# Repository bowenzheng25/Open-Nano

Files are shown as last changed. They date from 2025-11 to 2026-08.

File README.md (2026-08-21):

# Open Nano

This repository describes how to build and use your own nanopositioner. 

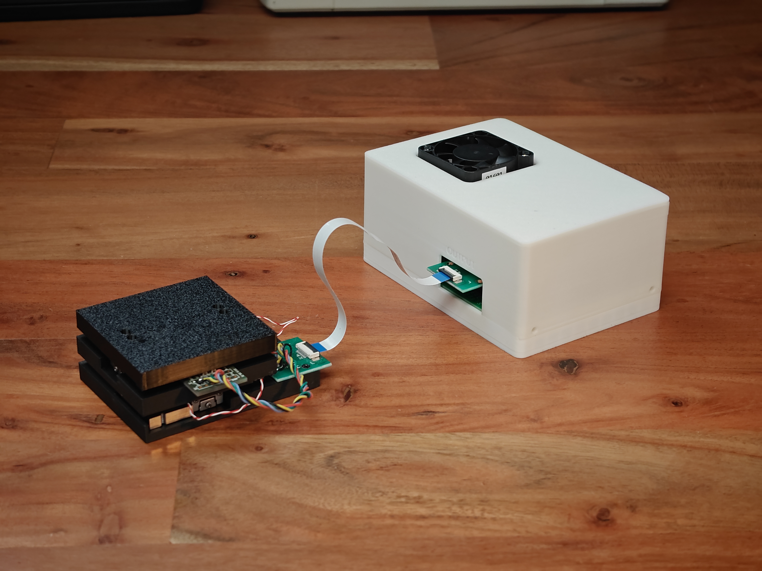
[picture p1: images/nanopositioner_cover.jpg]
nanopositioner assembly


## Getting Started

1.  Go over this readme file for high-level overview
2.  Obtain the parts listed in the [Bill of Materials](https://github.com/bwnzhng/Open-Nano/blob/main/assembly/bom.md)
3.  Assemble the instrument and electronics
4.  Configure the hardware to fit your needs
5.  Upload firmware using VSCode with PlattformIO plugin
6.  Calibrate axis

## Design Files

Files (ie .stl and .dxf) for your reproduction are saved in [the assembly folder](https://github.com/bwnzhng/Open-Nano/tree/main/assembly/cad)

The CAD files are produced in Fusion360. You can get free access through the educational license. 

Otherwise, engineering drawings are attached for you to reproduce the part in your choice of CAD software as the designs are relatively straightforward.

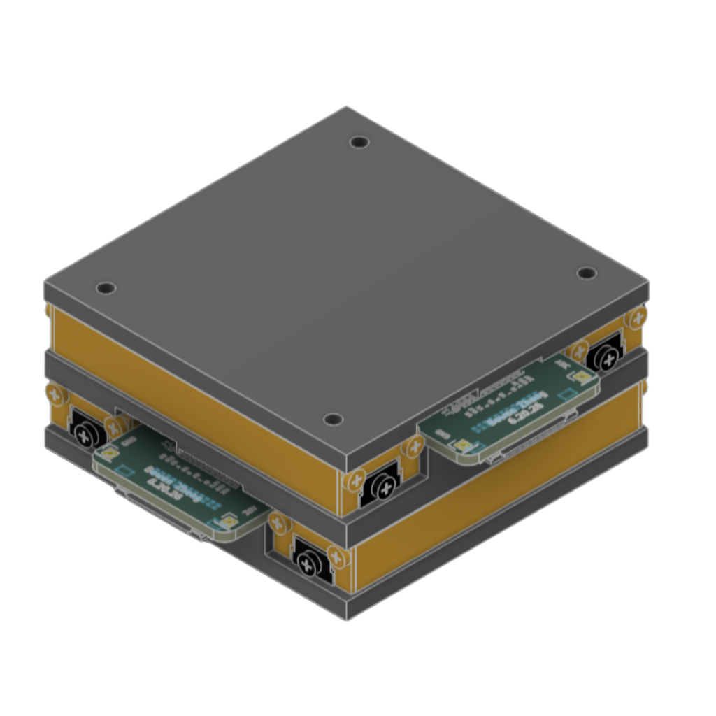
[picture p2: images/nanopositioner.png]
Nanopositioner

## Electronics

The PCB schematics are designed in KICAD. No SMD soldering is required since through hole electronic components are used for easier hands-on assembly.

Please note you will need to attach heatsinks to the amplifiers to maintain optimal performance.

This repository also contains fabrication files that can directly uploaded to a PCB manufacturer (located in [the electronics folder](https://github.com/bwnzhng/Open-Nano/tree/main/electronics))

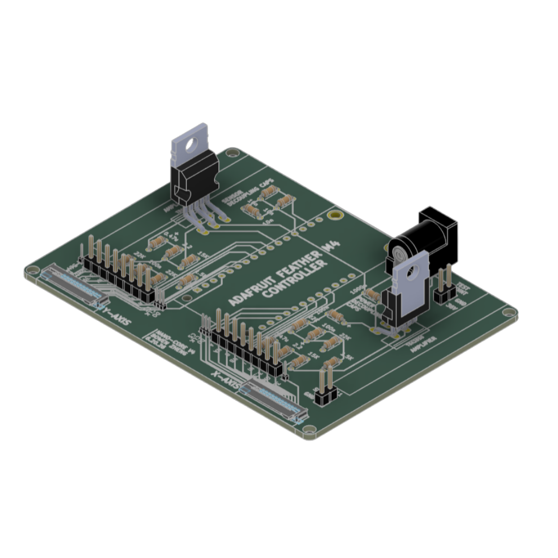
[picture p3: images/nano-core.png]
Nano-core electronics
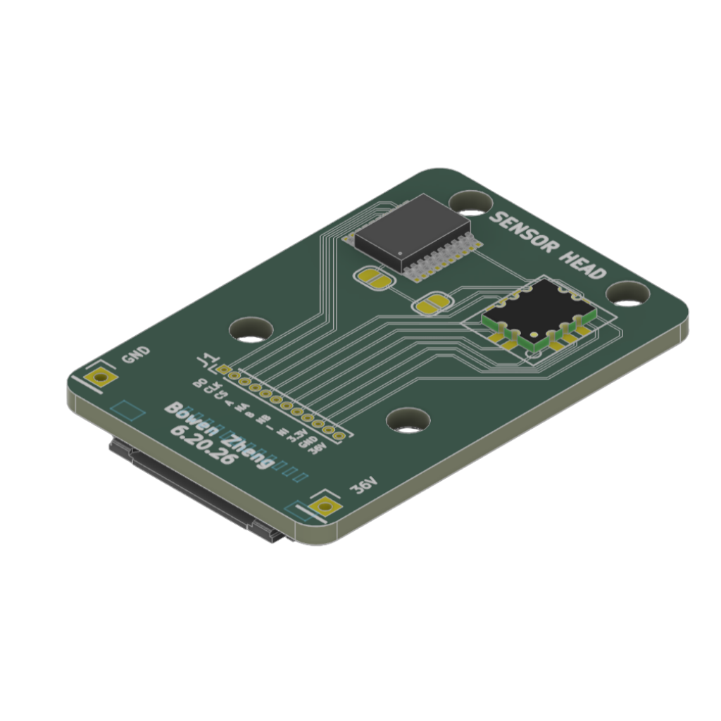
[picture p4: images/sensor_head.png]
Sensor head electronics


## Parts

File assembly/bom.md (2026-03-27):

# Bill of Materials (BOM)

## Nanopositioner Hardware
| Name | Qty | Description | Comments | Suggested link | Image |
|------|-----|-------------|----------|----------------|-------|
| X Stage | 1 |  |  3D print or machine out of aluminum. For convenience, order through JLCCNC (see jlccnc_order folder) | | |
| Y Stage | 1 |  |  3D print or machine out of aluminum. For convenience, order through JLCCNC (see jlccnc_order folder) | | |
| Sample Stage | 1 |  | 3D print or machine out of aluminum. For convenience, order through JLCCNC (see jlccnc_order folder) | | |
| Flexure | 2 |  | Manufacture using Wire EDM or waterjet. For convenience, order through JLCCNC (see jlccnc_order folder) | | |
| Linear Ball Slide (LS852) | 2 | Travel = 25 mm | Can switch out for longer/shorter travel | [Misumi](https://us.misumi-ec.com/vona2/detail/221000089462/?HissuCode=LS852&srsltid=AfmBOorXj1KnsJp_ueJ8ylQubgWb2TH5S-mg2W2aANUJIghY7beoXeTk&tab=catalog&Page=1)|
| Magnetic Tape | 1 | Length = 100 mm | Need to cut into two 40 mm long strips using steel bandsaw | [Alibaba](https://www.aliexpress.us/item/3256802636079698.html?spm=a2g0o.order_detail.order_detail_item.4.99a3f19cTgTQIm&gatewayAdapt=glo2usa)|
| Posic Encoder Tape | 1 | Length = 100 mm | Order through JLCPCB | 
| Feeler Gauge Set | 1 | | | [Amazon](https://www.amazon.com/CHERALKEST-Stainless-Thickness-0-0015-0-035-Thicknesses/dp/B0DBPND9PB/ref=sxts_b2b_sx_reorder_acb_business?content-id=amzn1.sym.93dc5330-3850-4554-84ea-5a8297a3e1d7%3Aamzn1.sym.93dc5330-3850-4554-84ea-5a8297a3e1d7&crid=IAURJS4AGTA4&cv_ct_cx=feeler+gauge&keywords=feeler+gauge&pd_rd_i=B0DBPND9PB&pd_rd_r=cb7d6be3-5ae8-4395-9047-53ab592f65d7&pd_rd_w=SMq0G&pd_rd_wg=lpIXX&pf_rd_p=93dc5330-3850-4554-84ea-5a8297a3e1d7&pf_rd_r=0FPR6B8PVMB7FMN0W969&qid=1752095035&sbo=RZvfv%2F%2FHxDF%2BO5021pAnSA%3D%3D&sprefix=feeler+gaug%2Caps%2C122&sr=1-1-76dd0896-e18a-4d36-b921-52fc00e57159)| |
| M2 Flat Head Phillips Screw | 26 | Length = 6 mm | | [Amazon](https://www.amazon.com/dp/B0D2R6Q3PW?ref=ppx_yo2ov_dt_b_fed_asin_title&th=1)| |
| M2 Nut | 4 |  | | [Amazon](https://www.amazon.com/FOCMKEAS-Stainless-Hexagon-Fasteners-Hardware/dp/B0CR7WCP4Z/ref=sr_1_13?crid=FTXC7P1HD8D7&dib=eyJ2IjoiMSJ9.kyW0zD-kPAR2yQPkfflajx2Yv8dZd0LYqbpKw7MGCtKoUtt8xwlEJKEyQO-AN5EZQE2ivn9_NPHnHzlnOkNZgygkMXUpK7X4EqwoyO7CyuKtkNQr_-coyxgS8b-4Ndga3oaT75ypX2EkE8tXMAcPPdtFs6EDo94jA5vdoX7HSAi9LFPcsEMN9hLfbYua__NpGmomLbidyUST53K8ZnK1PcvAclIU92uxx8cQU0o2sogx1E-aZhAISsdkqM9fwcXLBAApUu4IFrKsuS2SUHCzD6Y1ptwDZNIZFAwq3RoN1qo.Jqvi7EIAB0rQ5QqIQerQD-dx7zIbwmj0qJJDCWGTHkU&dib_tag=se&keywords=m2%2Bnut&qid=1762147830&s=industrial&sprefix=m2%2Bnu%2Cindustrial%2C273&sr=1-13&th=1)| |
| Piezoelectric Actuator | 2 | 2 x 3 x 10 mm | | [Micromechatronics](https://www.mmech.com/tokin-actuators/nec-tokin-resin-coated/nec-ae0203d08f)|

## Controller Hardware
| Name | Qty | Description | Comments | Suggested link | Image |
|------|-----|-------------|----------|----------------|-------|
| Magnetic Encoder AS5311 | 2 | Resolution = 0.5 mm |  | [Digikey](https://www.digikey.com/en/products/detail/ams-osram-usa-inc/AS5311-ATST-500/5892379?_gl=1*1ck5u6a*_up*MQ..*_gs*MQ..&gclid=CjwKCAjwspPOBhB9EiwATFbi5IlpicVnNmimVVWMThn-xvXitkn79nSTKi1qkFIgR1InyTzgiMlGPxoC3BYQAvD_BwE&gclsrc=aw.ds&gbraid=0AAAAADrbLlizLFmAgBv4Uc2WDGaBvEtGQ)| |
| Posic Encoder PO1030 | 2 | Resolution = 20 nm |  | [Posic](https://www.posicoder.com/product-page/inductive-encoder-chip-highspeed-PO1030)| |
| Adafruit Feather M4 Express | 1 | Microcontroller |  | [Adafruit](https://www.adafruit.com/product/3857?srsltid=AfmBOoq8kWYTsfTr7qERoHBVpf76dr8P1W41JnvQelL8GpSYsY70A2Qa)| |
| Piezo Driver (PDu150) | 1 | 3-Channel Low-Noise Amplifier | | [PiezoDrive](https://www.piezodrive.com/product/pdu150-three-channel-ultra-low-noise-150v-piezo-driver/) |
| 24V Power Adapter | 1 | Power Supply|  | [Amazon](https://www.amazon.com/100-240V-Converter-Transformer-Switching-5-5mmx2-5mm/dp/B09281KTS8/ref=sr_1_3?crid=25QPVHFO7FQ6F&dib=eyJ2IjoiMSJ9.uX9aOM0OfPL0K3NLP4LsJXjq6WpikWQ43RPZ70NumW82fGZj9xn4d9mUUGH1eDwqpU1YuFuSOO5UpKtq6tz9ZiIMIz6ZgJk1vt5bi5ZP6YmTyq_Gg8QKpBwXgwzfYAzVjyWWgIcGUYX18uB9uYvbYL055Zq82kjqFGbyPFNx_E14trX1YDl5C9TVpX5GojEWUlED9zwuyqHksBrk9MU8Iv-Uyz0LoUbk2Mp8aTF1YkRRlbPF8-A7zKq2CdjYt310ULgWxgHhkcHAiHRM10KNLanTPktntNDGlGiZdW3UXfI.WgrZRfmRdwP4dTFiHzx2icuTDWyn86JdO4BGGoYxNg4&dib_tag=se&keywords=24V+power+supply&qid=1753477511&s=electronics&sprefix=24v+power+supply%2Celectronics%2C97&sr=1-3) | |
| USB-C to USB Cable | 1 | | To upload code from laptop to microcontroller | [Amazon](https://www.amazon.com/CableCreation-Braided-480Mbps-Compatible-MacBook/dp/B0744BKDRD/ref=sxin_15_pa_sp_search_thematic-asin_sspa?content-id=amzn1.sym.ab2f90ad-3f8d-43ce-ac3a-7446bd8192fd%3Aamzn1.sym.ab2f90ad-3f8d-43ce-ac3a-7446bd8192fd&crid=3PAQT3QNNHENS&cv_ct_cx=usbc%2Bto%2Bmicro%2Busb&keywords=usbc%2Bto%2Bmicro%2Busb&pd_rd_i=B0744BKDRD&pd_rd_r=2c0fa0ed-9acd-4404-930e-f6f1b1fa45e6&pd_rd_w=1akTB&pd_rd_wg=cGuY8&pf_rd_p=ab2f90ad-3f8d-43ce-ac3a-7446bd8192fd&pf_rd_r=BS8GV0HJCFB9P8PX5P4D&qid=1762148746&s=electronics&sbo=RZvfv%2F%2FHxDF%2BO5021pAnSA%3D%3D&sprefix=usb%2Bto%2Bmicro%2Busb%2Celectronics%2C271&sr=1-1-baa1f287-65d3-41a3-a655-8bbba0531537-spons&sp_csd=d2lkZ2V0TmFtZT1zcF9zZWFyY2hfdGhlbWF0aWM&th=1)| |
| Power Barrel Jack | 1 | 2.5 mm OD | Plugs in with 24V power supply | [DigiKey](https://www.digikey.com/en/products/detail/same-sky-formerly-cui-devices-/PJ-002B/96965?gclsrc=aw.ds&gad_source=1&gad_campaignid=17336967819&gbraid=0AAAAADrbLliyNjnc33lOoBusgAsg1bauY&gclid=CjwKCAjwq9rFBhAIEiwAGVAZP3zd2ftnDtaAwOKfvE_ZYB8oU99MGMDRD6hTu-XzpnservrpLIKnpBoCEtYQAvD_BwE)||
| Flexible Flat Cable | 2 | 12 Pin |  | [Amazon](https://www.amazon.com/dp/B07RVD1RVZ?ref=ppx_yo2ov_dt_b_fed_asin_title) |
| Header Pins | 1 | Pitch = 2.54 mm | Will need to cut | [Amazon](https://www.amazon.com/dp/B0CN14TP2T?ref=ppx_yo2ov_dt_b_fed_asin_title) |
| 12 Pin Ribbon Connector | 4 | 1 mm pitch |  | [Digikey](https://www.digikey.com/en/products/detail/molex/2005280120/12142065?_gl=1*1v4ucj8*_up*MQ..*_gs*MQ..&gclid=Cj0KCQiArt_JBhCTARIsADQZaylmHfRX2gHj1Ykv_0Os5uXvxeybIM7TGLqFyKkRFnrJ3mXZQNeHVF0aAuiREALw_wcB&gclsrc=aw.ds&gbraid=0AAAAADrbLlgTcsxonNtgcFPO34hVIdP1s)| |
| 100 nF Capacitor | 1 | SMD | | [Digikey](https://www.digikey.com/en/products/detail/yageo/CC0603KRX5R8BB104/20376210) |
| 10 nF Capacitor | 1 | SMD | | [Digikey](https://www.digikey.com/en/products/detail/kemet/CAN12C103KAGACTU/16798068) |
| 1 uF Capacitor | 1 | SMD | | [Digikey](https://www.digikey.com/en/products/detail/kemet/C0402C105K9PACTU/1090778) |

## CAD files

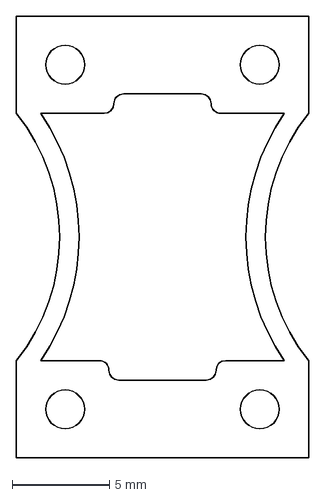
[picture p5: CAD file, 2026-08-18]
assembly/cad/dxf/Flexure Mount.dxf
15.0 x 22.7 mm

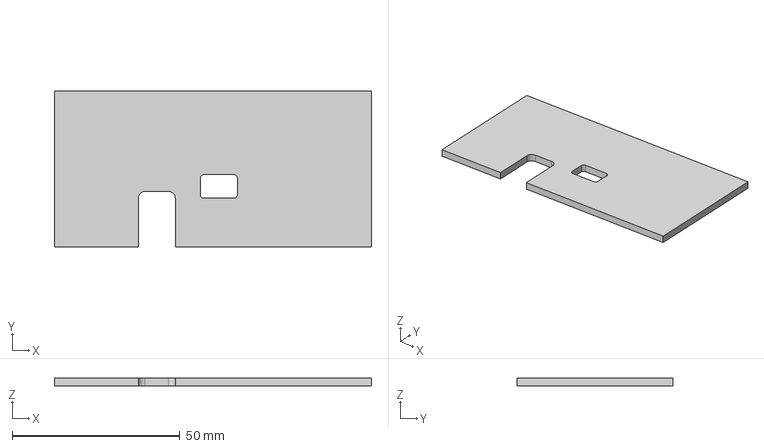
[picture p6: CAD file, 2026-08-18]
assembly/cad/step/PCB Front Panel.step
94.5 x 46.4 x 2.50 mm

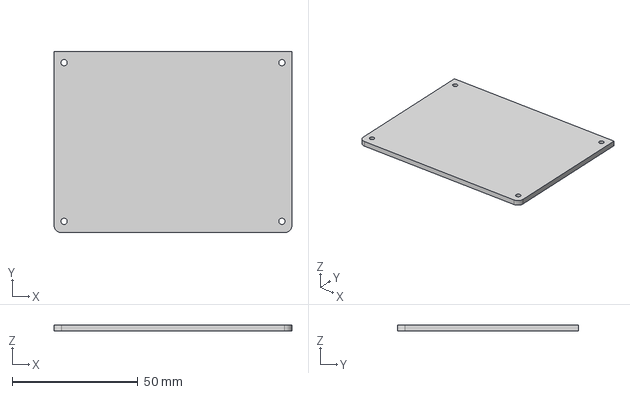
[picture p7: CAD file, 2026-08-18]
assembly/cad/step/PCB Base.step
94.5 x 72.0 x 2.50 mm

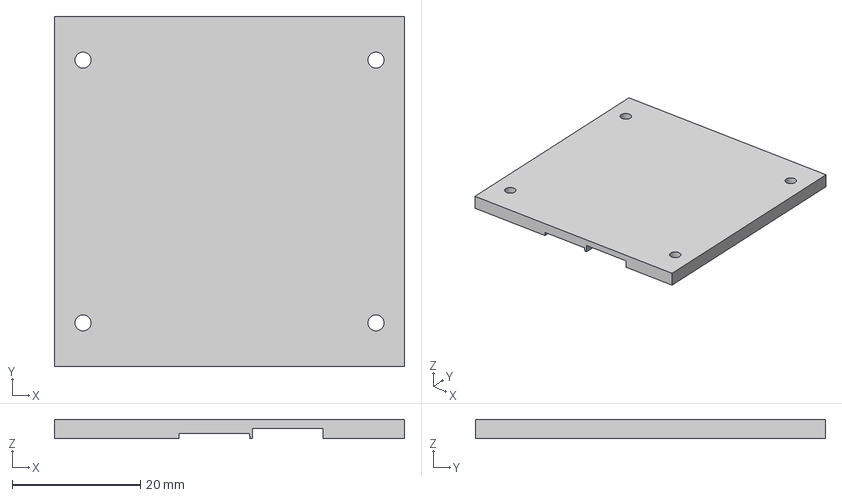
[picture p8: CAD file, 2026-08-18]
assembly/cad/step/Sample_Stage.step
54.6 x 54.6 x 3.00 mm

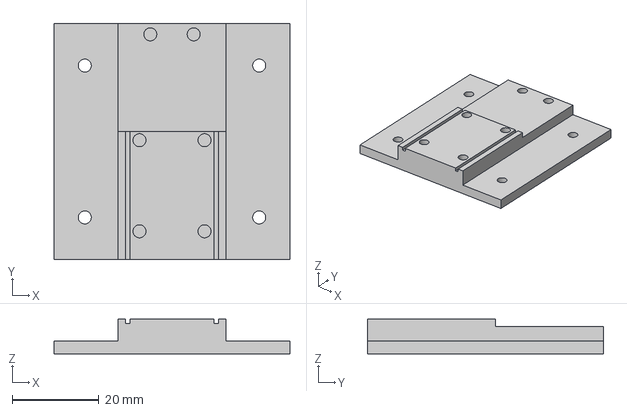
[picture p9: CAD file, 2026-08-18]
assembly/cad/step/X_Stage.step
54.4 x 54.4 x 8.00 mm

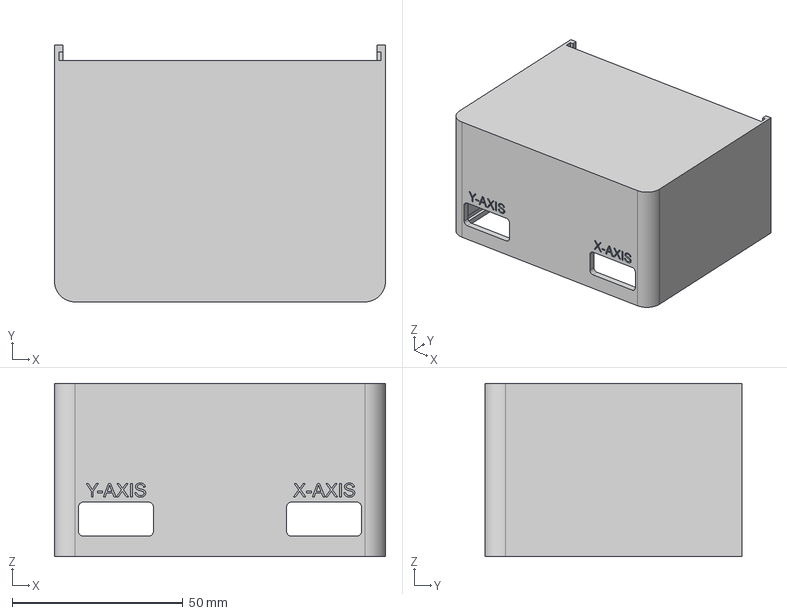
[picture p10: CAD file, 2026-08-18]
assembly/cad/step/PCB Top Enclosure.step
97.0 x 75.2 x 50.8 mm

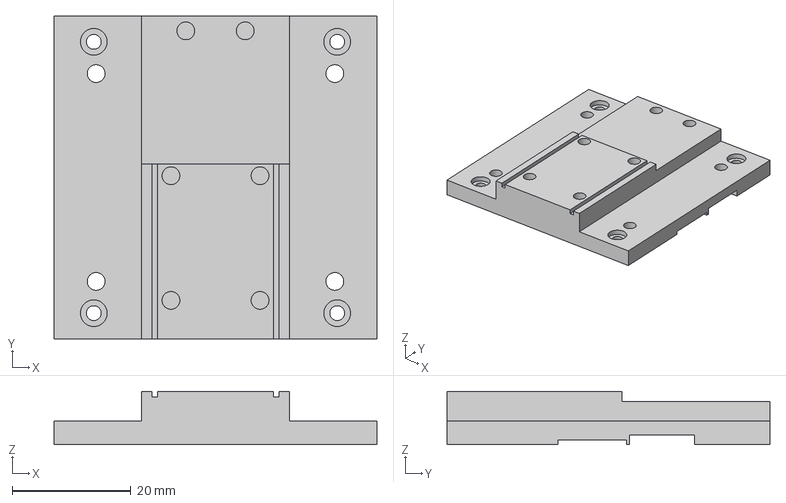
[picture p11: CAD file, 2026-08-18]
assembly/cad/step/Y_Stage.step
54.4 x 54.4 x 9.00 mm

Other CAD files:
assembly/cad/dxf/PCB Base.dxf
assembly/cad/dxf/PCB Front Panel.dxf
assembly/cad/f3d/Assembly.f3z
assembly/cad/f3d/Controller Assembly.f3z
assembly/cad/f3d/Flexure Mount.f3d
assembly/cad/f3d/PCB Base.f3d
assembly/cad/f3d/PCB Front Panel.f3d
assembly/cad/f3d/PCB Top Enclosure.f3d
assembly/cad/f3d/sample_stage.f3d
assembly/cad/f3d/x_stage.f3d
assembly/cad/f3d/y_stage.f3d

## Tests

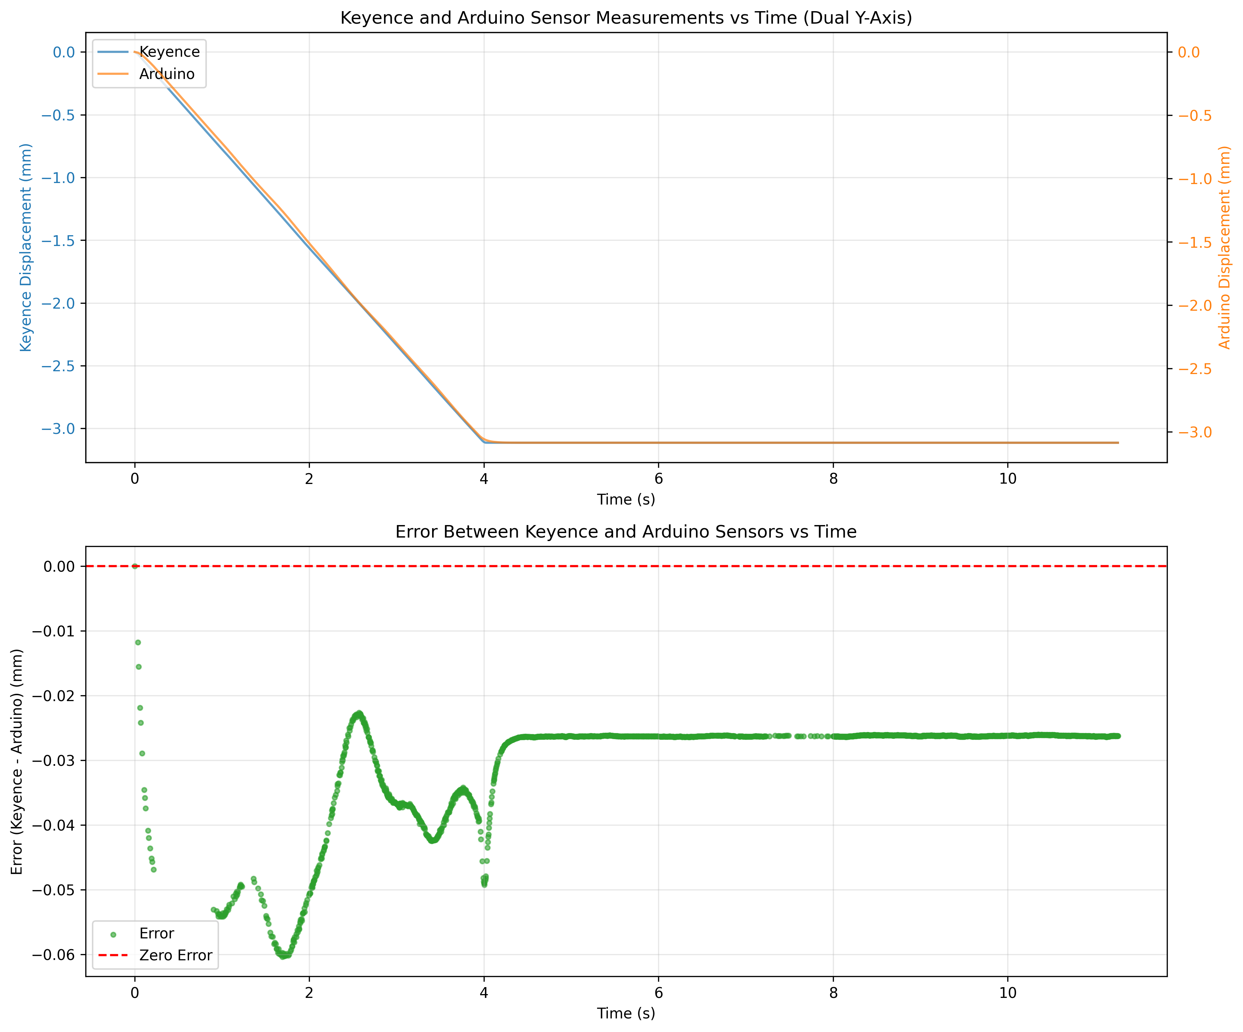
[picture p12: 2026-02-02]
testing/graphs/error_sensor10.png

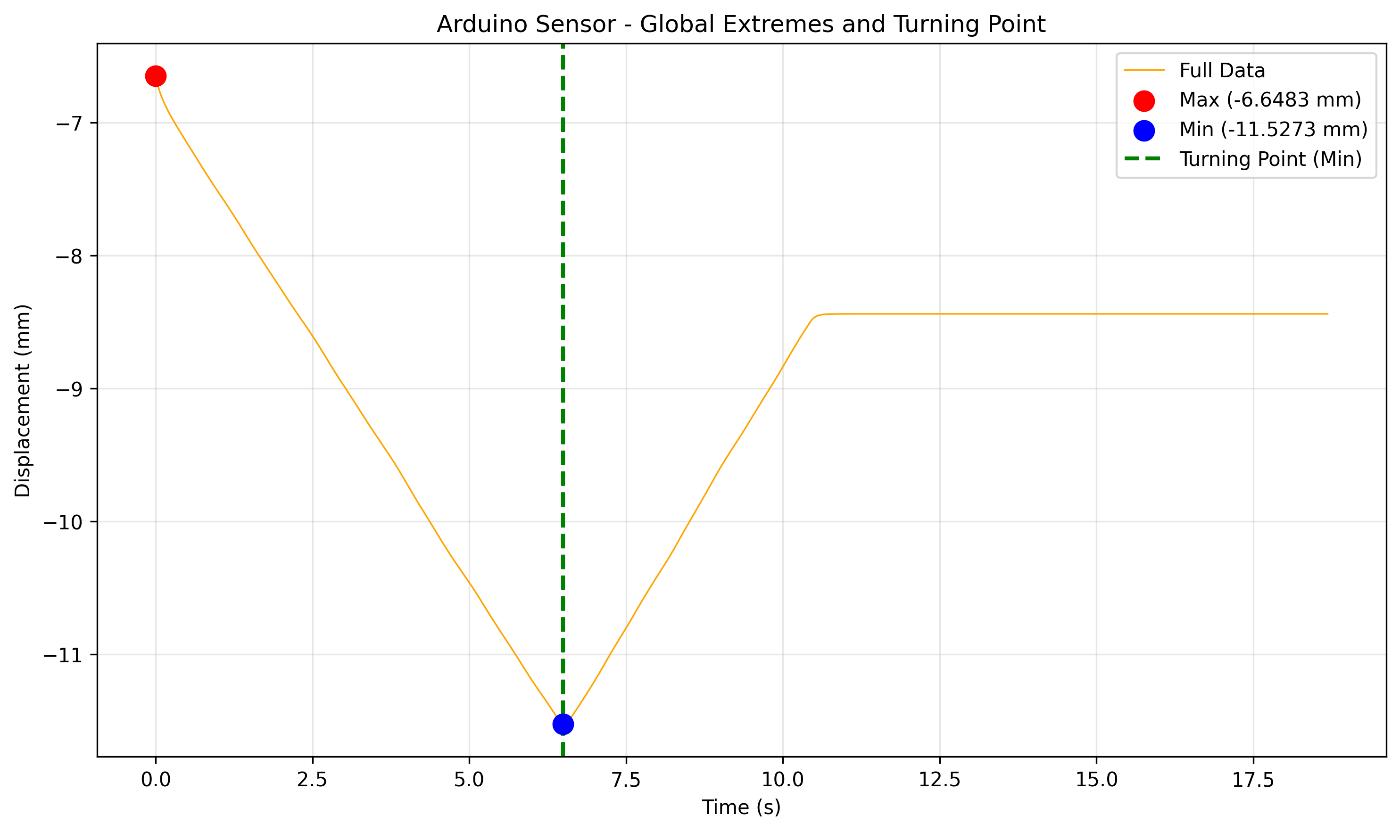
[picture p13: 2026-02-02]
testing/graphs/arduino_extremes10.png

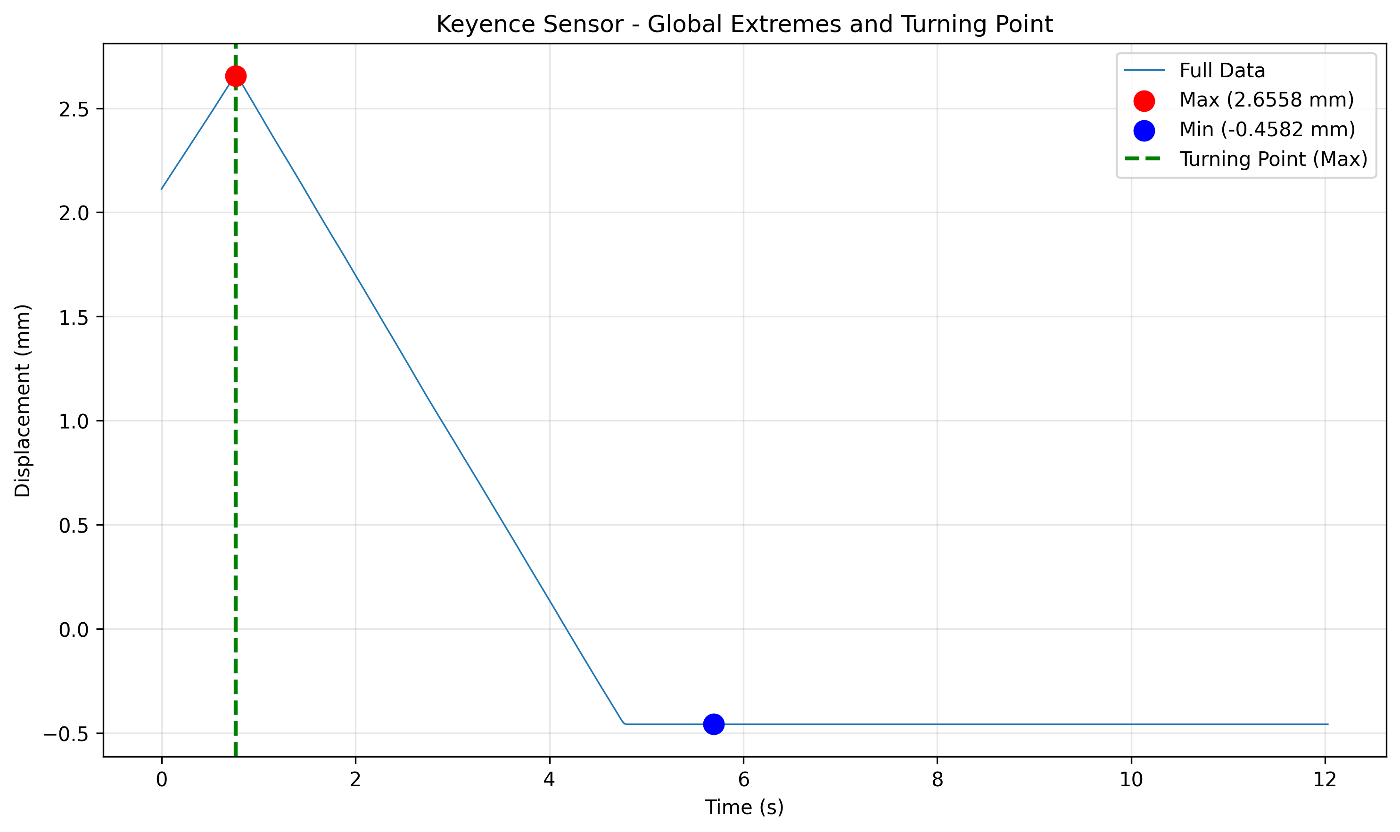
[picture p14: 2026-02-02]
testing/graphs/keyence_extremes10.png

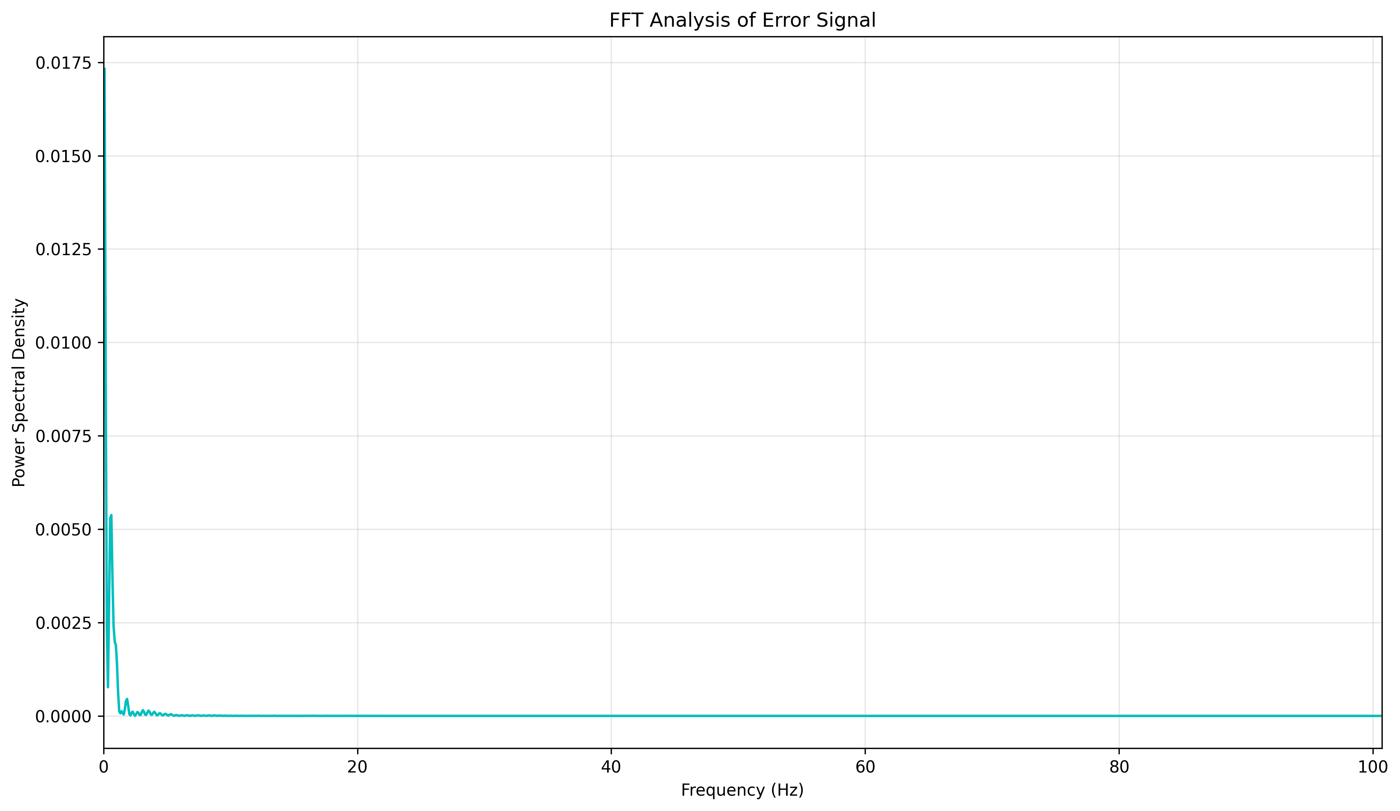
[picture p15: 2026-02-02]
testing/graphs/fft_sensor10.png

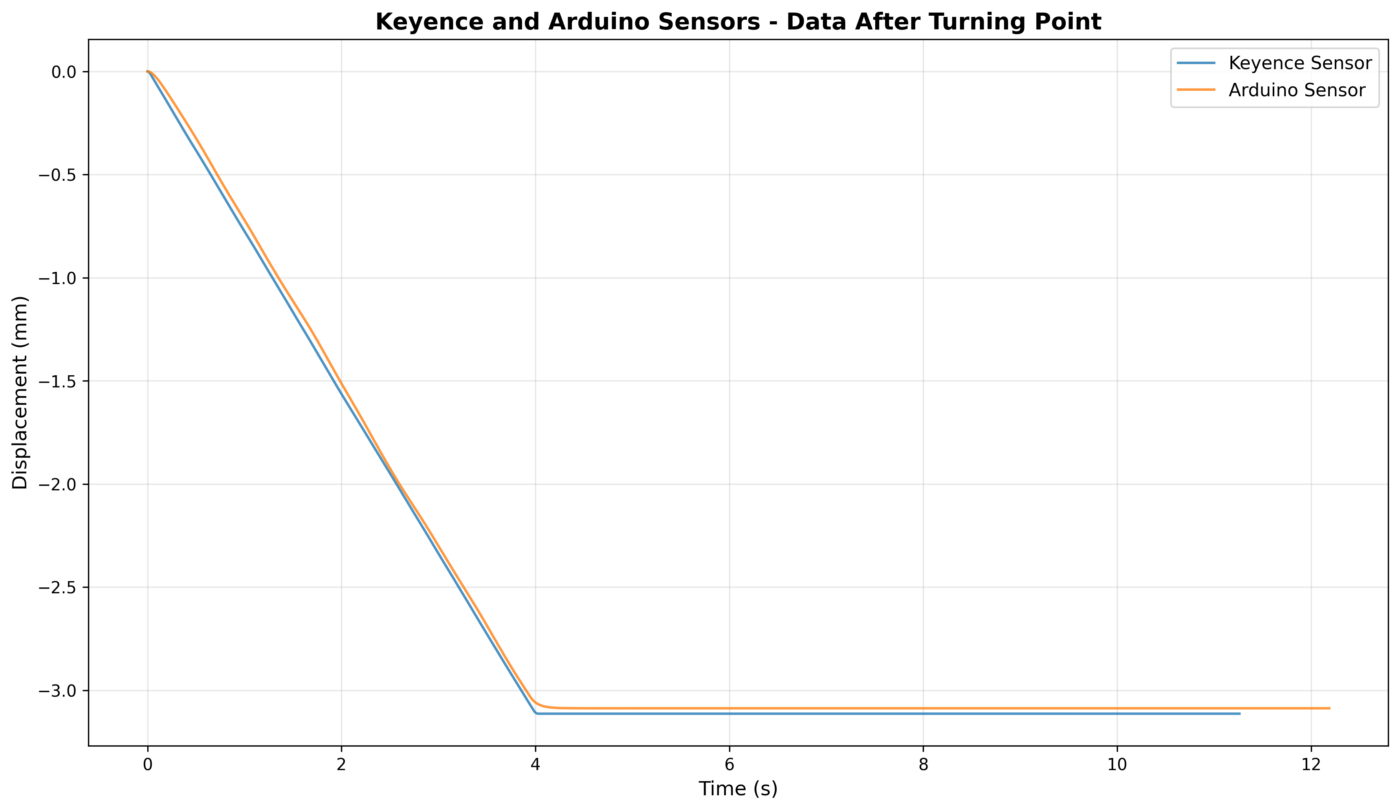
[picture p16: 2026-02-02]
testing/graphs/combined_sensors10.png

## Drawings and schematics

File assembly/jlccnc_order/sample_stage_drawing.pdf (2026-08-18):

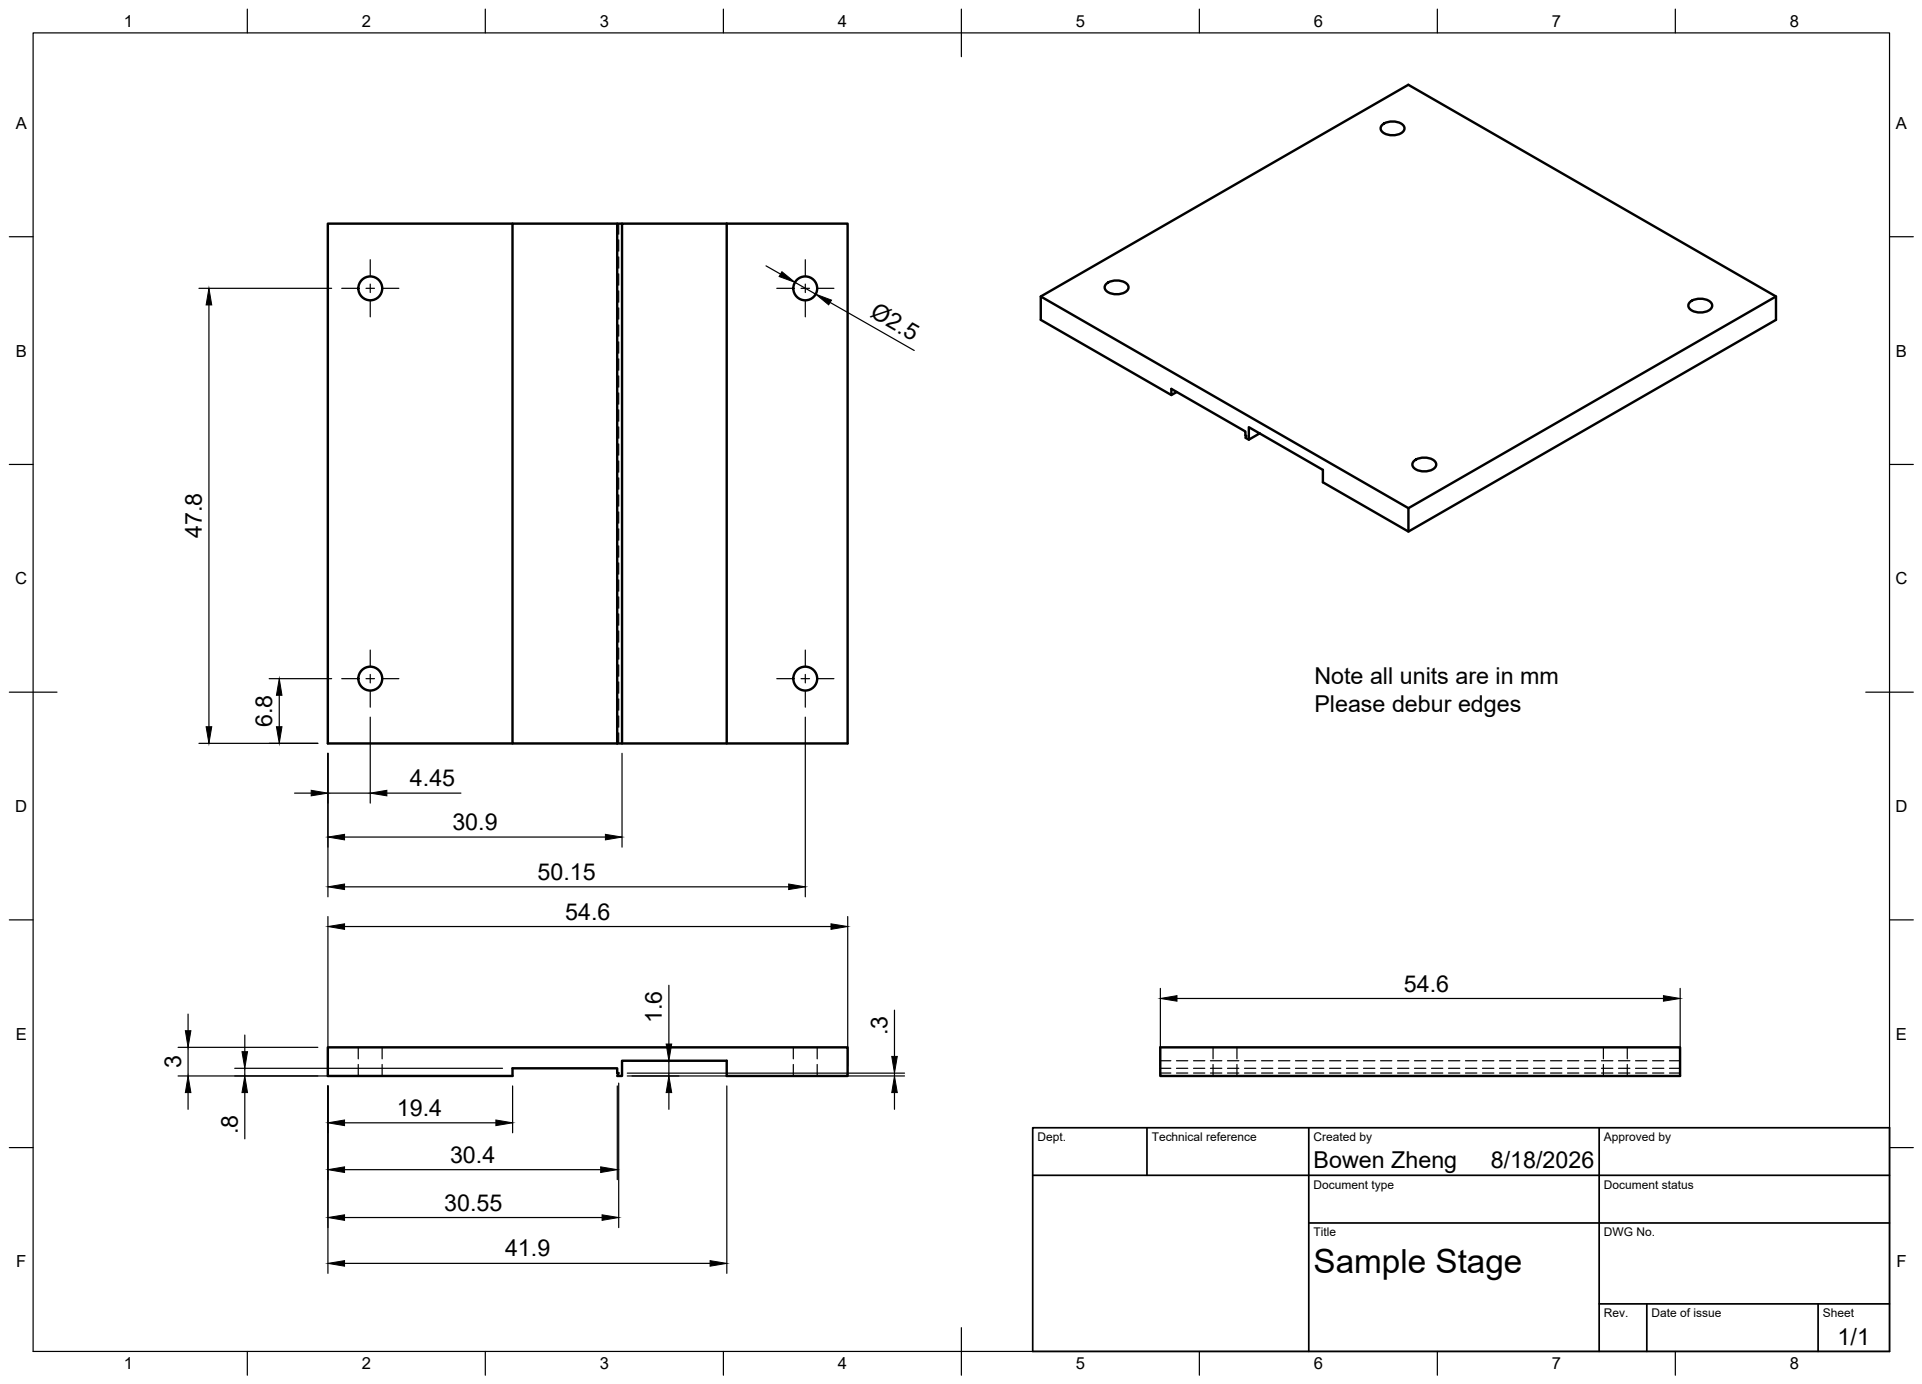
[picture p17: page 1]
Title; DWG No.; Rev.; Date of issue; Sheet; Sample Stage

Note all units are in mm
Please debur edges

Dept. | Technical reference | Created by Bowen Zheng 8/18/2026 | Approved by

Document type | Document status

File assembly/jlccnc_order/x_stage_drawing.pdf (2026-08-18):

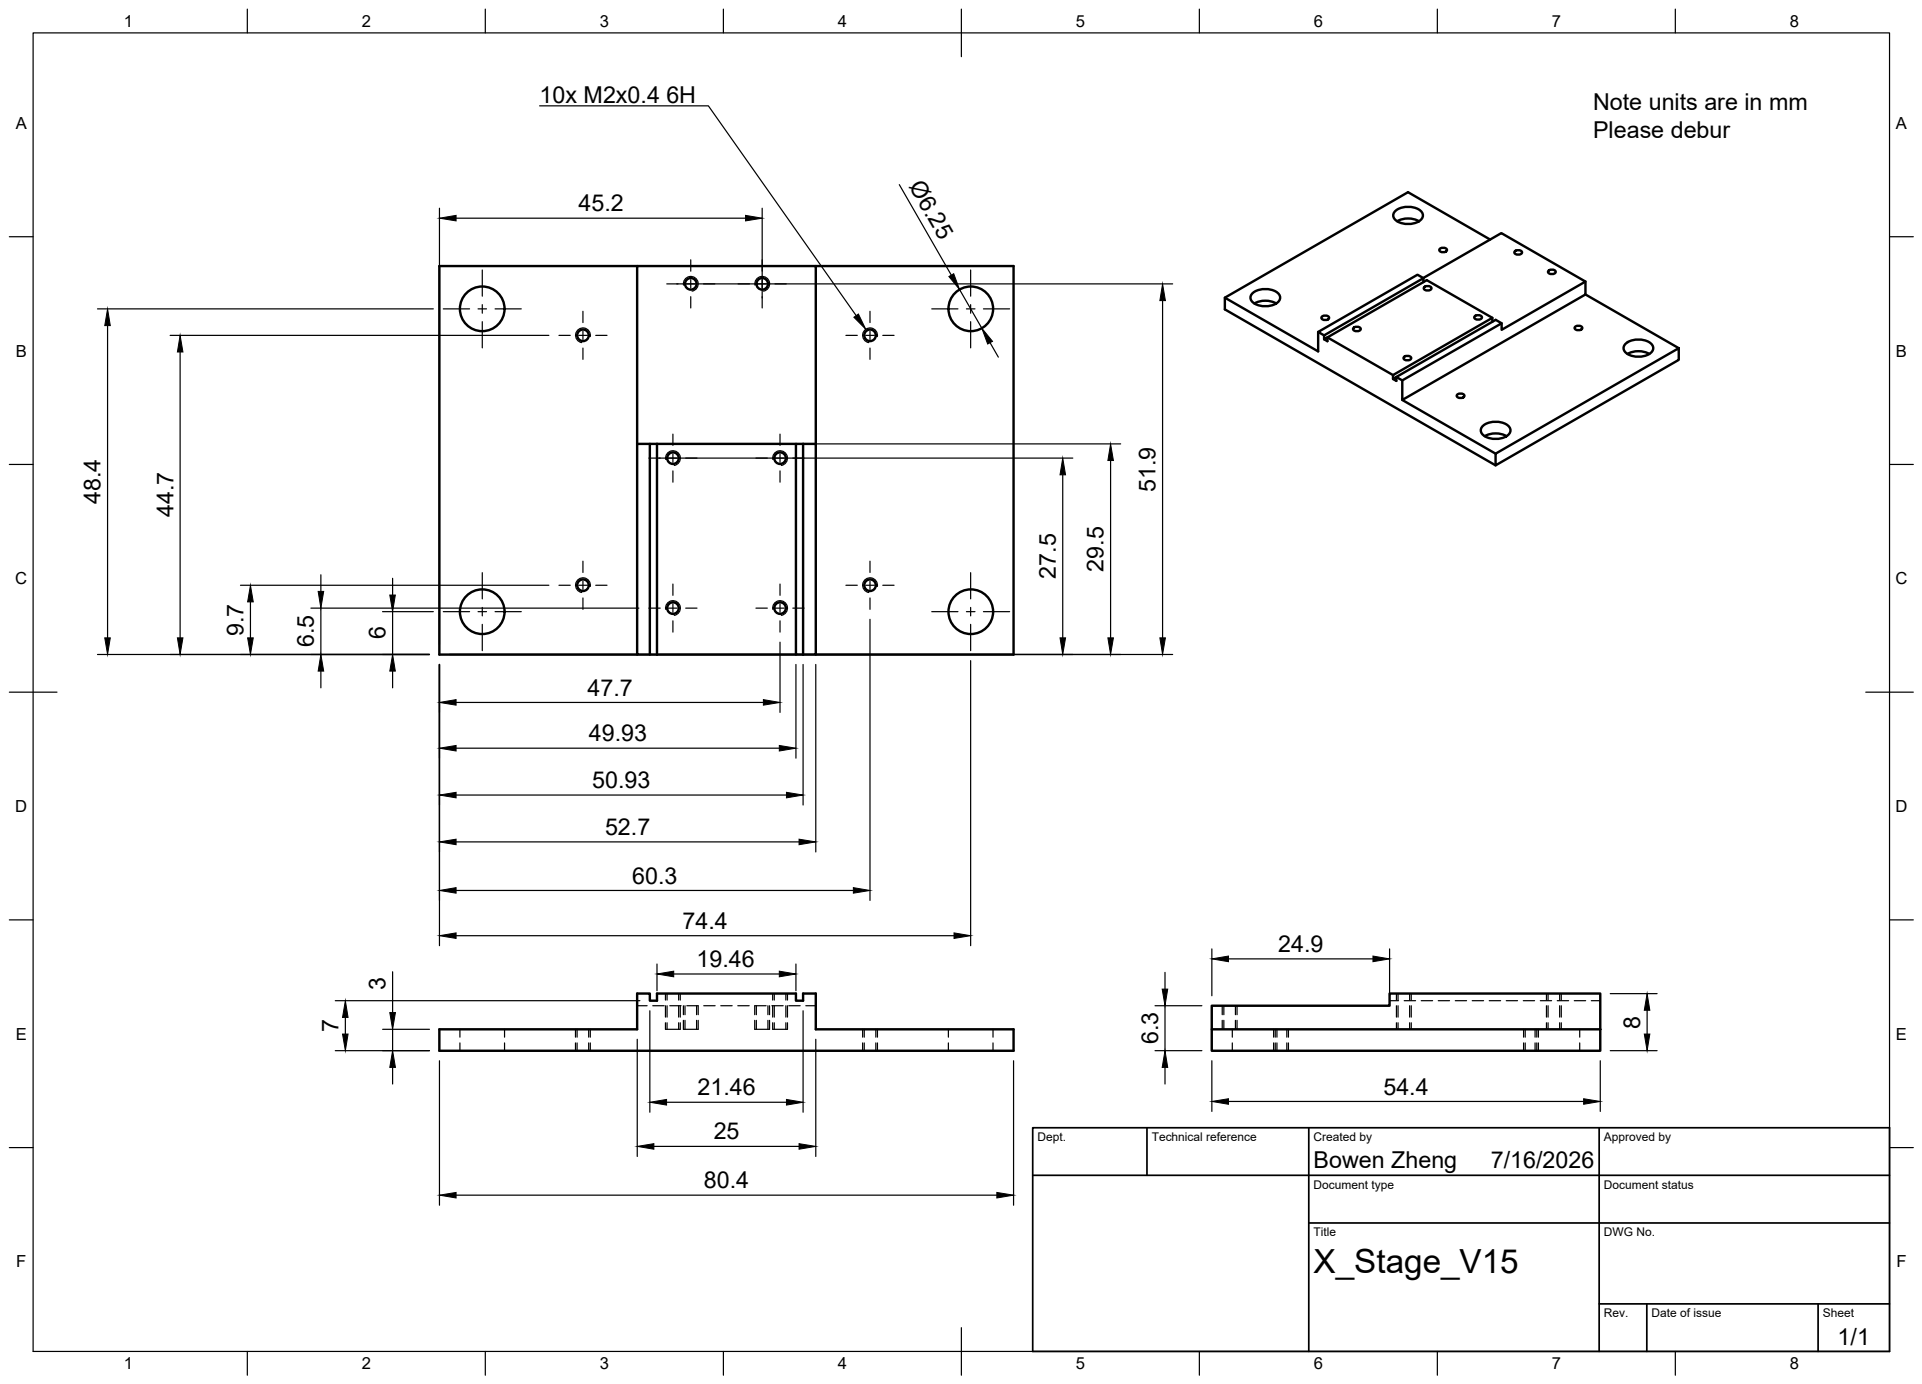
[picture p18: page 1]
Title; DWG No.; Rev.; Date of issue; Sheet

Note units are in mm
Please debur

Dept. | Technical reference | Created by Bowen Zheng 7/16/2026 | Approved by

Document type | Document status

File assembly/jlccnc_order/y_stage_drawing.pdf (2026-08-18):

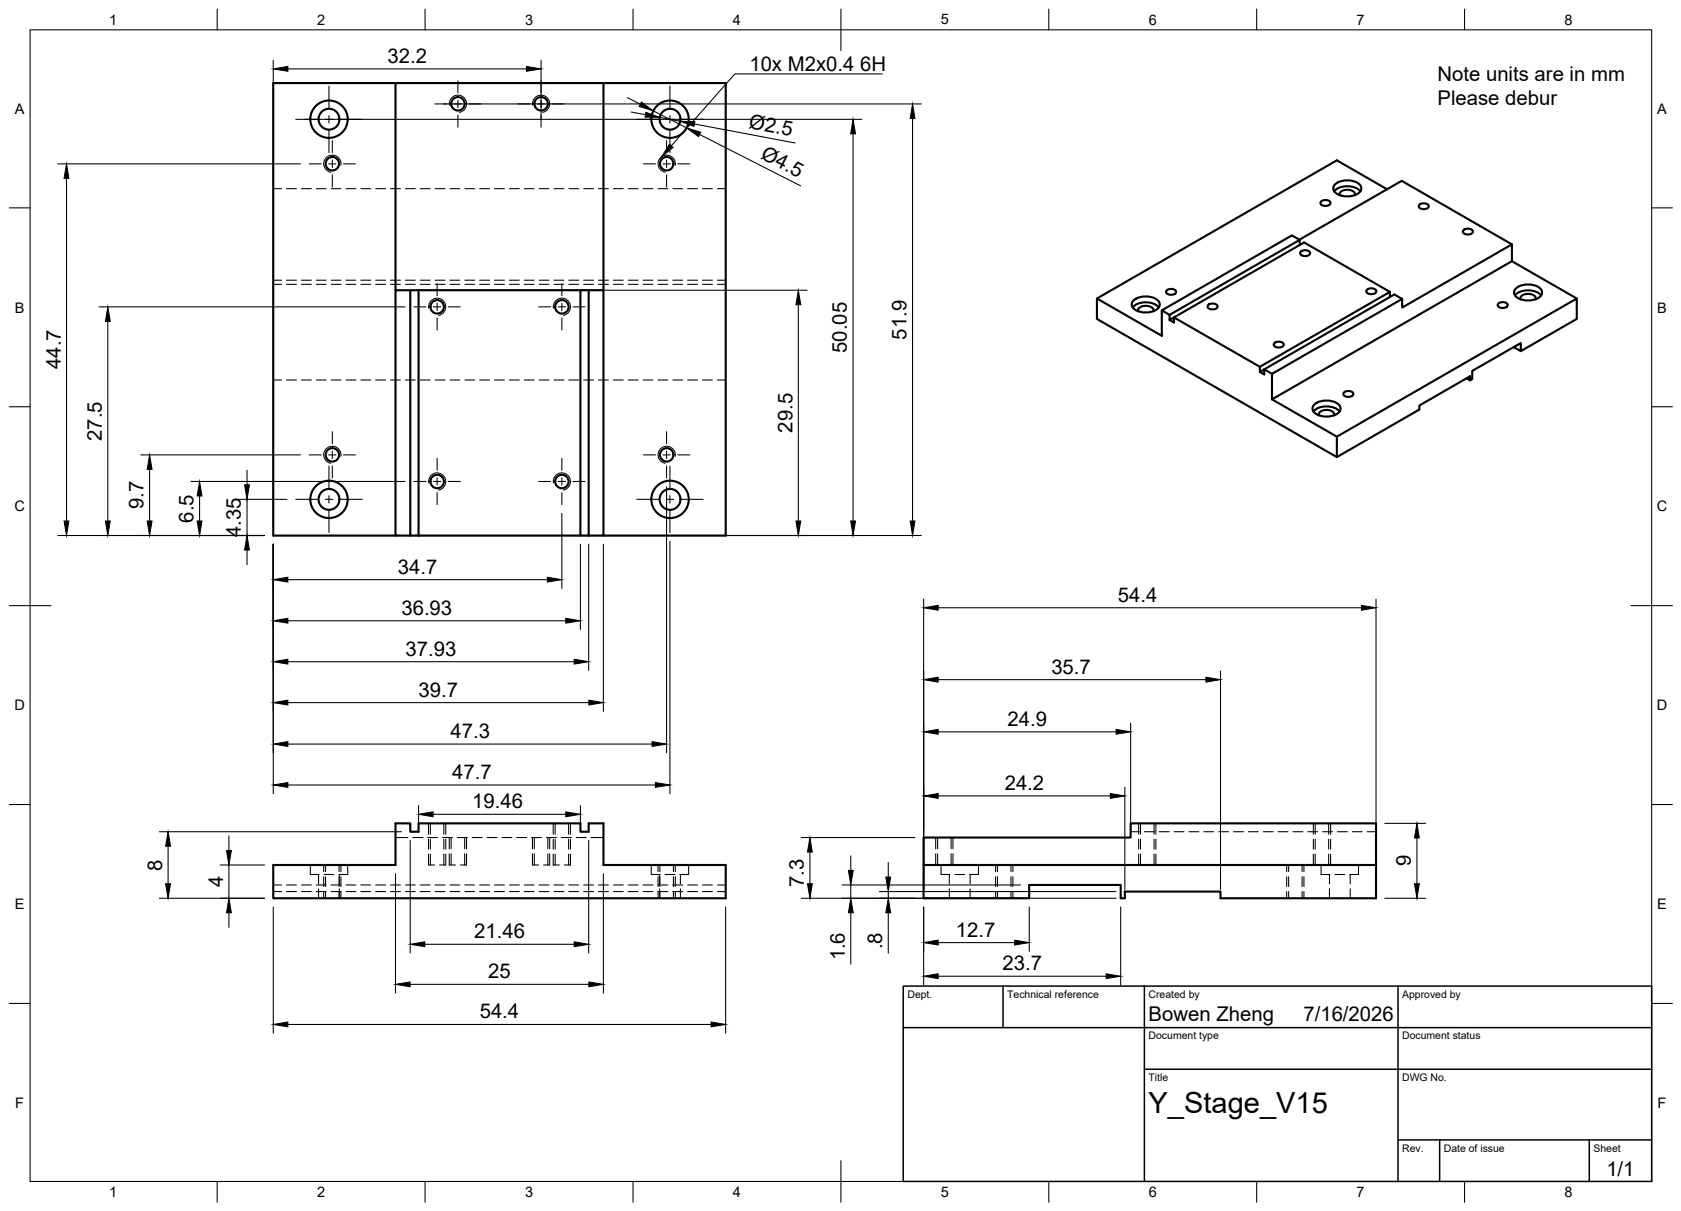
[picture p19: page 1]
Title; DWG No.; Rev.; Date of issue; Sheet; Bowen Zheng

Note units are in mm
Please debur

Dept. | Technical reference | Created by 7/16/2026 | Approved by

Document type | Document status

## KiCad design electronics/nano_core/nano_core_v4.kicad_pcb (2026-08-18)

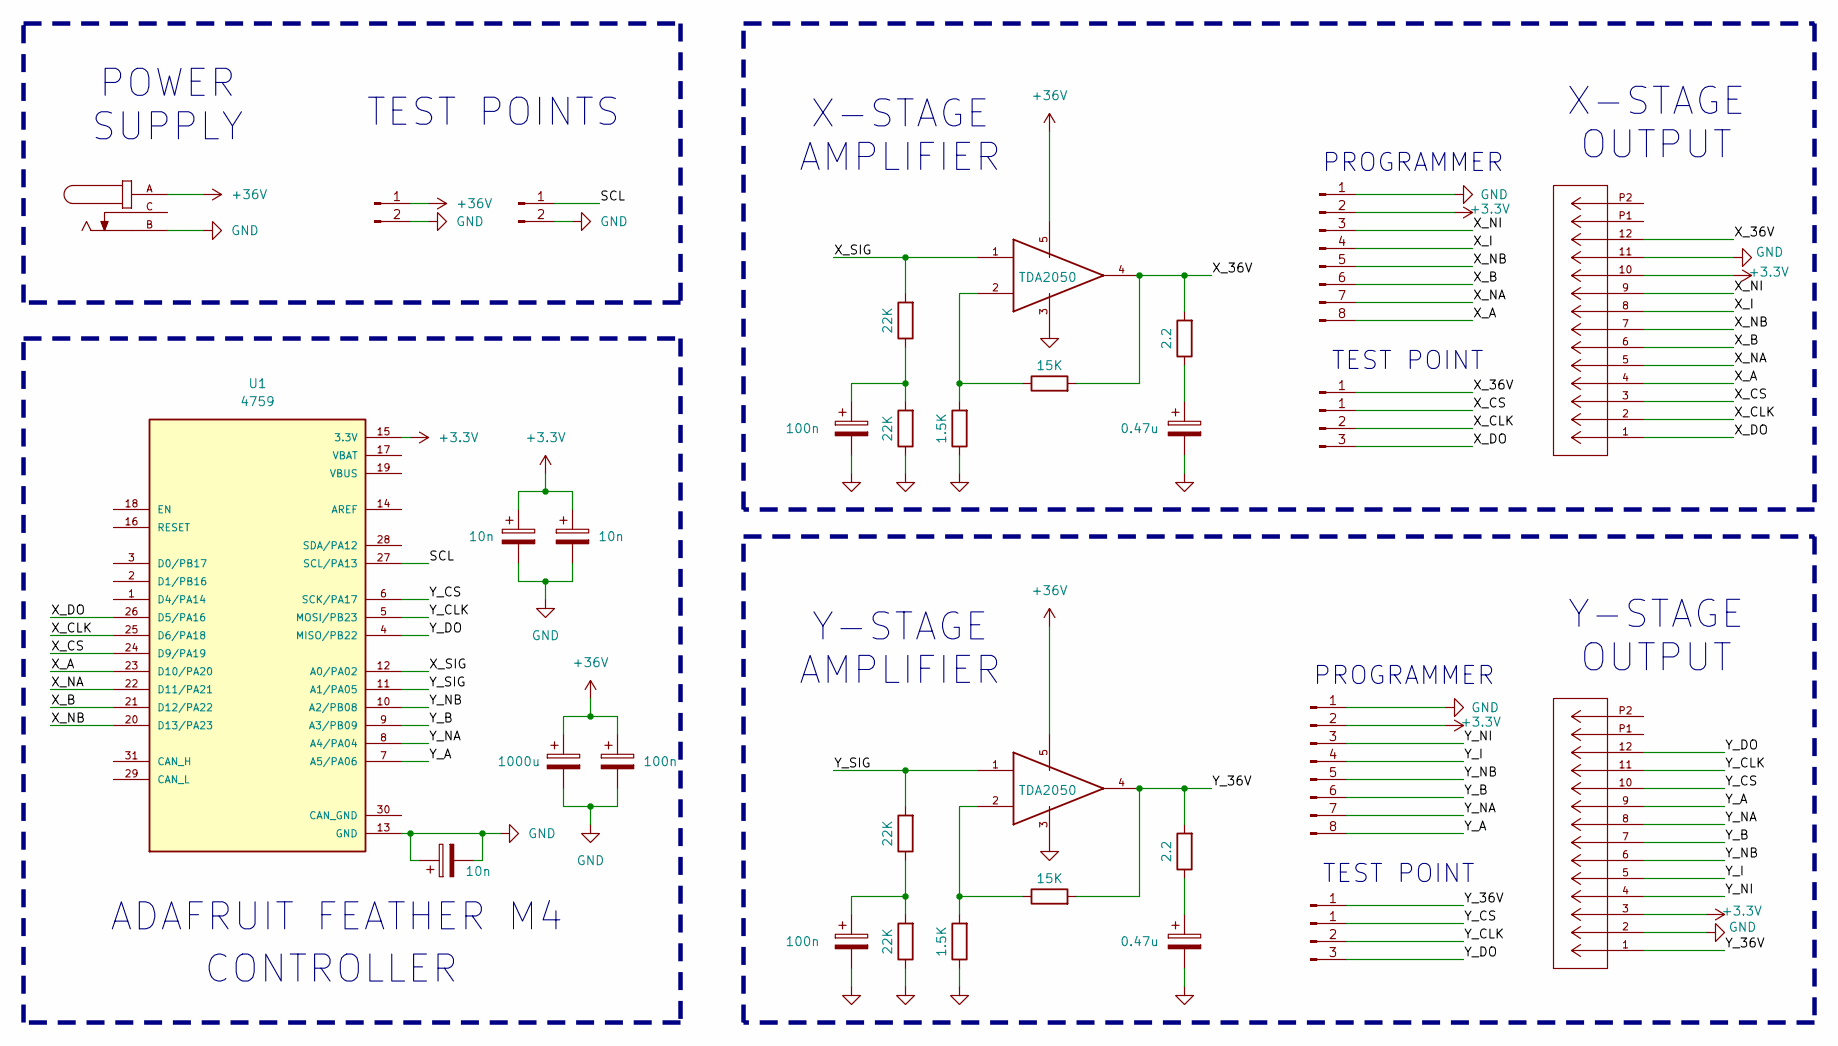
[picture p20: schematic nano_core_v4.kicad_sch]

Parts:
C1: 1000u; R_Axial_DIN0204_L3.6mm_D1.6mm_P5.08mm_Horizontal
C2, C4, C5: 100n; R_Axial_DIN0204_L3.6mm_D1.6mm_P5.08mm_Horizontal
C3, C8: 0.47u; R_Axial_DIN0204_L3.6mm_D1.6mm_P5.08mm_Horizontal
C9, C10, C11: 10n; R_Axial_DIN0204_L3.6mm_D1.6mm_P5.08mm_Horizontal
J1, J11: Conn_01x02_Pin; PinHeader_1x02_P2.54mm_Vertical
J2, J3: 2005280120; CON_2005280120_MOL; MANUFACTURER_PART_NUMBER 2005280120
J4, J5: Conn_01x08_Pin; PinHeader_1x08_P2.54mm_Vertical
J6: 54-00166; TENSILITY_54-00166; PARTREV A
J7, J9: Conn_01x01_Pin; PinHeader_1x01_P1.00mm_Vertical
J8, J10: Conn_01x03_Pin; PinHeader_1x03_P1.00mm_Vertical
R1, R9: 15K; R_Axial_DIN0204_L3.6mm_D1.6mm_P5.08mm_Horizontal
R2, R10: 2.2; R_Axial_DIN0204_L3.6mm_D1.6mm_P5.08mm_Horizontal
R3, R8: 1.5K; R_Axial_DIN0204_L3.6mm_D1.6mm_P5.08mm_Horizontal
R4, R5, R6, R7: 22K; R_Axial_DIN0204_L3.6mm_D1.6mm_P5.08mm_Horizontal
U1: 4759; MODULE_4759; PARTREV Dec. 08 2020
U2, U3: TDA2050; PENTAWATT

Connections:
+3.3V: C10.1, C11.1, J2.10, J3.3, J4.2, J5.2, U1.15 (3.3V)
+36V: C1.1, C2.1, J1.1, J6.A, U2.5 (SUPPLY_VOLTAGE), U3.5 (SUPPLY_VOLTAGE)
/SCL: J11.1, U1.27 (SCL/PA13)
/X_36V: J2.12, J7.1 (Pin_1_1), R1.2, R2.2, U2.4 (OUTPUT)
/X_A: J2.4, J4.8, U1.23 (D10/PA20)
/X_B: J2.6, J4.6, U1.21 (D12/PA22)
/X_CLK: J2.2, J8.2, U1.25 (D6/PA18)
/X_CS: J2.3, J8.1, U1.24 (D9/PA19)
/X_DO: J2.1, J8.3, U1.26 (D5/PA16)
/X_I: J2.8, J4.4
/X_NA: J2.5, J4.7, U1.22 (D11/PA21)
/X_NB: J2.7, J4.5, U1.20 (D13/PA23)
/X_NI: J2.9, J4.3
/X_SIG: R5.2, U1.12 (A0/PA02), U2.1 (NONINVERTING)
/Y_36V: J3.1, J9.1 (Pin_1_1), R9.2, R10.2, U3.4 (OUTPUT)
/Y_A: J3.9, J5.8, U1.7 (A5/PA06)
/Y_B: J3.7, J5.6, U1.9 (A3/PB09)
/Y_CLK: J3.11, J10.2, U1.5 (MOSI/PB23)
/Y_CS: J3.10, J10.1, U1.6 (SCK/PA17)
/Y_DO: J3.12, J10.3, U1.4 (MISO/PB22)
/Y_I: J3.5, J5.4
/Y_NA: J3.8, J5.7, U1.8 (A4/PA04)
/Y_NB: J3.6, J5.5, U1.10 (A2/PB08)
/Y_NI: J3.4, J5.3
/Y_SIG: R6.2, U1.11 (A1/PA05), U3.1 (NONINVERTING)
GND: C1.2, C2.2, C3.2, C4.2, C5.2, C8.2, C9.1, C9.2, C10.2, C11.2, J1.2, J2.11, J3.2, J4.1, J5.1, J6.B, J11.2, R3.1, R4.1, R7.1, R8.1, U1.13 (GND), U2.3 (GND), U3.3 (GND)
unnamed: C3.1, R2.1
unnamed: C4.1, R4.2, R5.1
unnamed: C5.1, R6.1, R7.2
unnamed: C8.1, R10.1
unnamed: R1.1, R3.2, U2.2 (INVERTING)
unnamed: R8.2, R9.1, U3.2 (INVERTING)

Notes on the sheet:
Y-STAGE AMPLIFIER
Y-STAGE OUTPUT
CONTROLLER
PROGRAMMER
TEST POINT
TEST POINTS
POWER SUPPLY
X-STAGE OUTPUT
X-STAGE AMPLIFIER
ADAFRUIT FEATHER M4

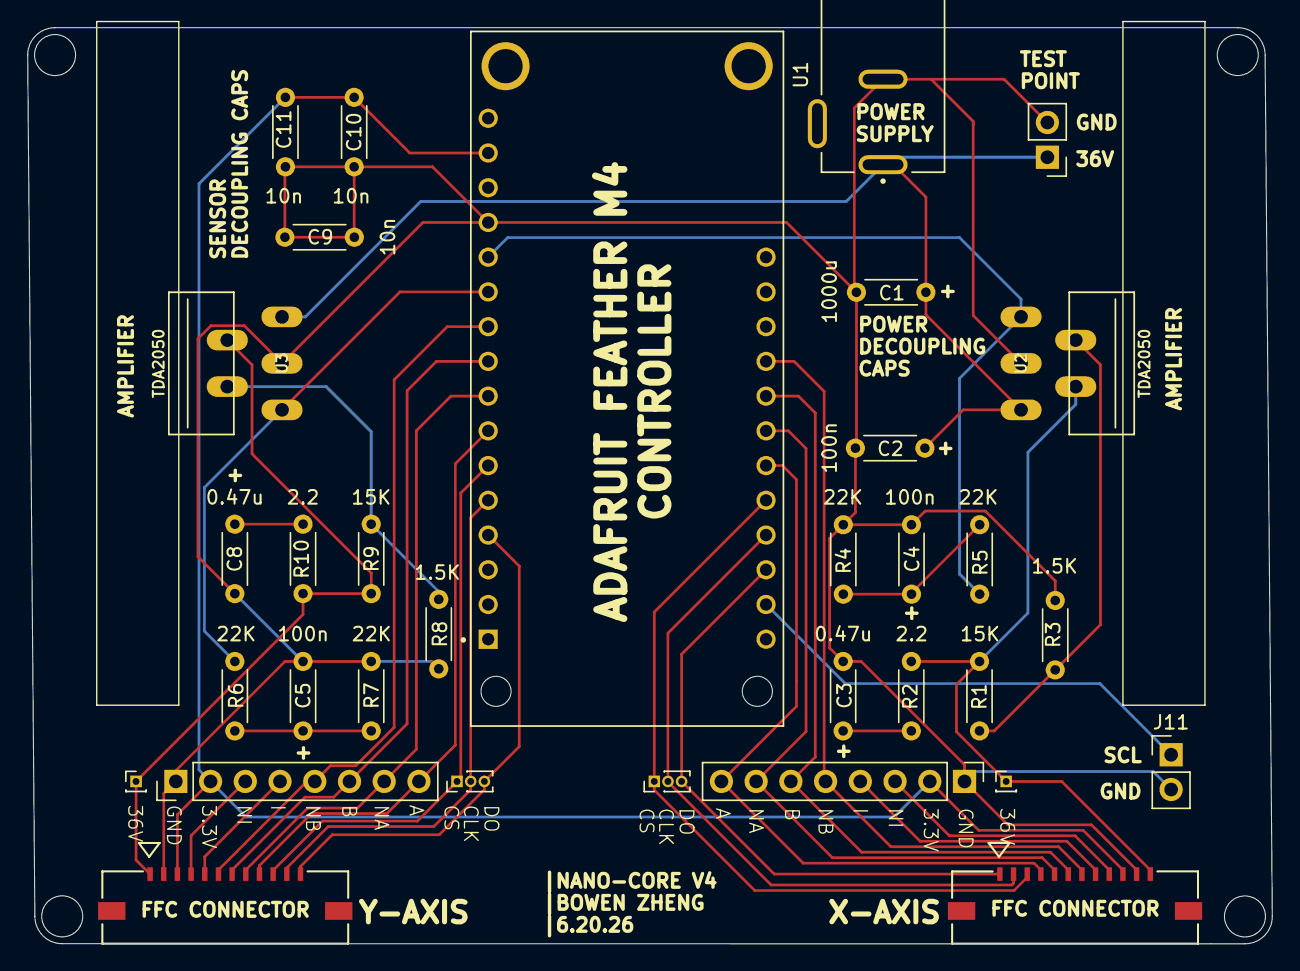
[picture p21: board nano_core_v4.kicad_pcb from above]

Board: 2 copper layers, 91.0 x 67.0 mm, 33 parts (0 on the bottom side), 32 nets.

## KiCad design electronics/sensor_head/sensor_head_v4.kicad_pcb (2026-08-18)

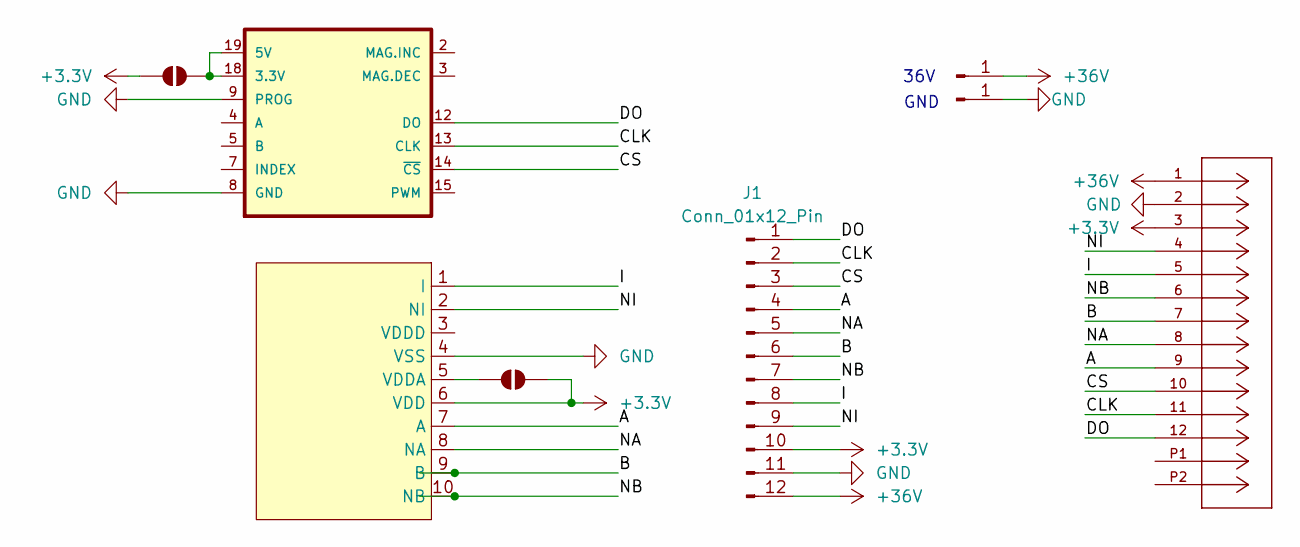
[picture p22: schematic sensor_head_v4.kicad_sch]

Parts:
J1: Conn_01x12_Pin; PinHeader_1x12_P1.00mm_Vertical
J2: 2005280120; CON_2005280120_MOL; MANUFACTURER_PART_NUMBER 2005280120
J3, J4: Conn_01x01_Pin; PinHeader_1x01_P2.54mm_Vertical
JP3, JP4: SolderJumper_2_Open; SolderJumper-2_P1.3mm_Open_RoundedPad1.0x1.5mm
U3: AS5311; TSSOP.20
U4: posic_1030

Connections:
+3.3V: J1.10, J2.3, JP3.1 (A), JP4.2 (B), U4.6 (VDD)
+36V: J1.12, J2.1, J3.1 (Pin_1_1)
/A: J1.4, J2.9, U4.7 (A)
/B: J1.6, J2.7, U4.9 (B)
/CLK: J1.2, J2.11, U3.13 (CLK)
/CS: J1.3, J2.10, U3.14 (~CS)
/DO: J1.1, J2.12, U3.12 (DO)
/I: J1.8, J2.5, U4.1 (I)
/NA: J1.5, J2.8, U4.8 (NA)
/NB: J1.7, J2.6, U4.10 (NB)
/NI: J1.9, J2.4, U4.2 (NI)
GND: J1.11, J2.2, J4.1 (Pin_1_1), U3.8 (GND), U3.9 (PROG), U4.4 (VSS)
unnamed: JP3.2 (B), U3.18 (3.3V), U3.19 (5V)
unnamed: JP4.1 (A), U4.5 (VDDA)

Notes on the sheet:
GND
36V

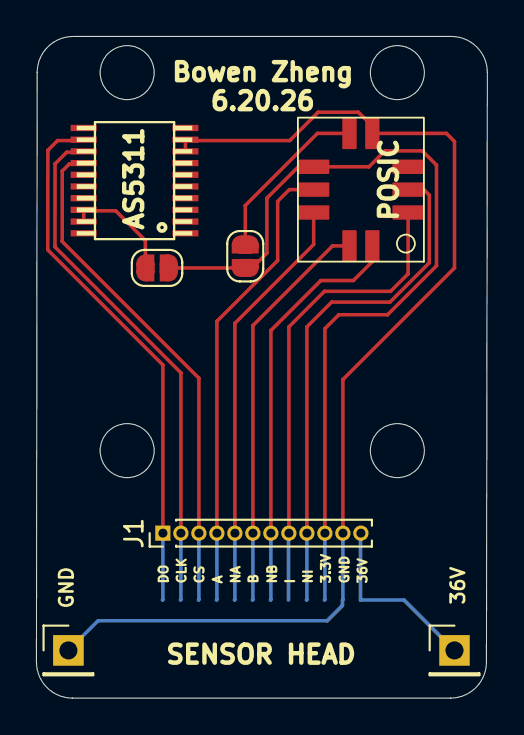
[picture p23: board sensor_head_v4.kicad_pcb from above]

Board: 2 copper layers, 25.1 x 36.8 mm, 8 parts (1 on the bottom side), 14 nets.

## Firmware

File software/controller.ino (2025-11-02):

#include <Arduino.h>
#include <timers.h>
#define DEADBAND 1.0F

// MAGNETIC SENSOR INITIALIZATION
const int X_CS = A2;
const int X_CLK = A3;
const int X_DO = A4;
const int Y_CS = A5;
const int Y_CLK = 25;
const int Y_DO = 24;

// STATE MACHINE
const int CALIBRATE = 1;
const int READ = 2;
const int MOVE = 3;
const int OPEN = 4;
const int WAIT = 5;
int state = CALIBRATE;
int old_state = CALIBRATE;
bool axis_state = 0;       // 0 is X axis, 1 is Y axis
bool unusedXFlag = true;   // For tracking if offset is used
bool unusedYFlag = true;   // For tracking if offset is used
bool readComplete = false; // Checks if reading is complete before moving stages

// CALIBRATION
struct AxisStatus {
  volatile int piezoPosition;
  volatile int oldPiezoPosition;
  volatile int newPiezoPosition;
  volatile int offsetVal;
  bool calibrationDone;
  unsigned long startTime;
};

// INITIALIZING POSITION TRACKING
#define NUM_AXES 2  // X, Y
AxisStatus axes[NUM_AXES] = {
  { -15000, 0, 0, 0, false, 0 },  // X
  { -15000, 0, 0, 0, false, 0 },  // Y
};

const int calibrateRange = 2;
// unsigned long startTime         = 0;
const unsigned long duration = 2000;  // 2 seconds in milliseconds
const int startingFrequencyX = 700;
const int startingFrequencyY = -700;
const float countsToMicrons = 0.48828125;  // 2000 microns/2^12 counts

// FOR PID CONTROL
unsigned long executionDuration = 0;  // [microseconds] Time between this and the previous loop execution.  Variable used for integrals and derivatives
unsigned long lastExecutionTime = 0;  // [microseconds] System clock value at the moment the loop was started the last time
int targetXPosition = 0, targetYPosition = 0;
float positionErrorX = 0, positionErrorY = 0;
float integralErrorX = 0, integralErrorY = 0;
float velocityErrorX = 0, velocityErrorY = 0;
float desiredFrequencyX = 0, desiredFrequencyY = 0;
float piezoVelocityX = 0, piezoVelocityY = 0;
int previousPiezoPositionX = 0, previousPiezoPositionY = 0;
long previousVelCompTimeX = 0, previousVelCompTimeY = 0;
const int MIN_VEL_COMP_COUNT = 2;      // [encoder counts] Minimal change in piezo position that must happen between two velocity measurements
const long MIN_VEL_COMP_TIME = 10000;  // [microseconds] Minimal time that must pass between two velocity measurements
float KP = 1;                        // [Volt / encoder counts] P-Gain
float KD = 0.0005;                      // [Volt * seconds / encoder counts] D-Gain
float KI = 0;                      // [Volt / (encoder counts * seconds)] I-Gain

// Timing:
unsigned long startWaitTime;     // [microseconds] System clock value at the moment the WAIT state started
const long WAIT_TIME = 10000;  // [microseconds] Time waiting at each location
const int TARGET_BAND = 1;       // [encoder counts] "Close enough" range when moving towards a target.

// USER INPUT:
struct Coordinate {
  float xMicrons;
  float yMicrons;
  int xCounts;
  int yCounts;
};
int step_size_state = 0;
int targetX_open = 0;
int targetY_open = 0;
bool reached_pos = true;

#define NUM_COORDINATES 100
Coordinate coordinates[NUM_COORDINATES] = {
  {0, 0, 0, 0},
  {100, 100, 0, 0},
  {50, 50, 0, 0},
  {150, 150, 0, 0},
  {100, 100, 0, 0},
  {200, 200, 0, 0},
  {150, 150, 0, 0},
  {250, 250, 0, 0},
  {200, 200, 0, 0},
  {300, 300, 0, 0},
  {14000, 14000, 0, 0},
  {13950, 13950, 0, 0},
  {14450, 14450, 0, 0},
  {14400, 14400, 0, 0},
  {14900, 14900, 0, 0},
  {14850, 14850, 0, 0},
  {15350, 15350, 0, 0},
  {15300, 15300, 0, 0},
  {15800, 15800, 0, 0},
  {15750, 15750, 0, 0},
  {16250, 16250, 0, 0},
  {16200, 16200, 0, 0},
  {16700, 16700, 0, 0},
  {16650, 16650, 0, 0},
  {17150, 17150, 0, 0},
  {17100, 17100, 0, 0},
  {17600, 17600, 0, 0},
  {17550, 17550, 0, 0},
  {18050, 18050, 0, 0},
  {18000, 18000, 0, 0},
  {18500, 18500, 0, 0},
  {18450, 18450, 0, 0},
  {18950, 18950, 0, 0},
  {18900, 18900, 0, 0},
  {19400, 19400, 0, 0},
  {19350, 19350, 0, 0},
  {19850, 19850, 0, 0},
  {19800, 19800, 0, 0},
  {20300, 20300, 0, 0},
  {20250, 20250, 0, 0},
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
};
// Track which coordinate we're at:
int currentCoordinateIndex = 0; // Ignoring first one
// int currentCoordinateIndex = 1; // Ignoring first one

uint16_t read_bits(uint8_t dataPin, uint8_t clockPin, uint8_t bitOrder, uint8_t numBits) {
  uint16_t value = 0;
  uint16_t i;
  for (i = 0; i < numBits; i++) {
    digitalWrite(clockPin, HIGH);
    if (bitOrder == LSBFIRST) {
      delayMicroseconds(50);
      value |= digitalRead(dataPin) << i;
    } else {
      delayMicroseconds(50);
      value |= digitalRead(dataPin) << (numBits - 1 - i);
    }
    digitalWrite(clockPin, LOW);
  }
  return value;
}

int position_read(uint8_t csPin, uint8_t clockPin, uint8_t dataPin) {
  int position = 0;
  digitalWrite(clockPin, 1);
  digitalWrite(csPin, LOW);  // Start transfer
  digitalWrite(clockPin, 0);
  uint16_t read_position = read_bits(dataPin, clockPin, MSBFIRST, 12);
  uint8_t error = read_bits(dataPin, clockPin, MSBFIRST, 3);
  digitalWrite(csPin, HIGH);  // End transfer

  if (error == 4) {  // expect binary to be 100 to be good, which is 4 in decimal
    position = read_position;
    return position;
  } else {
    return position;
  }
}

int track_position(int current_pos, int new_pos, int old_pos, int index, bool offsetFlag, int offset) {
  int diff = new_pos - old_pos;
  if (offsetFlag & (unusedXFlag | unusedYFlag)) {
    current_pos = current_pos - offset;
    if (index == 0) {
      unusedXFlag = false;  // X is offsetted
    } else if (index == 1) {
      unusedYFlag = false;  // Y is offsetted
    }
  }
  if (abs(diff) > 4096 / 4) {  // wrap around occurred
    if (diff > 0) {            // backward motion occurred
      current_pos = current_pos - (4096 - new_pos) - old_pos;
    } else {  // forward motion occured
      current_pos = current_pos + (4096 - old_pos) + new_pos;
    }
  } else {  // no wrap around
    current_pos = current_pos + diff;
  }

  return current_pos;
}

void write_freqs(float hz_0, float hz_1) {
  // TODO: deadband... around zero...
  if (hz_0 < DEADBAND && hz_0 > -DEADBAND) {
    hz_0 = hz_0 < 0.0F ? -DEADBAND : DEADBAND;
  }
  if (hz_1 < DEADBAND && hz_1 > -DEADBAND) {
    hz_1 = hz_1 < 0.0F ? -DEADBAND : DEADBAND;
  }
  //
  float per_0 = 120000000.0F / (hz_0 * 4096.0F);
  float per_1 = 120000000.0F / (hz_1 * 4096.0F);
  //
  write_periods((int16_t)per_0, (int16_t)per_1);
}

void calibrateAxis(int axisIndex) {
  AxisStatus &axis = axes[axisIndex];
  if (axis.calibrationDone) return;

  if (axisIndex == 0) {
    axis.piezoPosition = position_read(X_CS, X_CLK, X_DO);
  } else if (axisIndex == 1) {
    axis.piezoPosition = position_read(Y_CS, Y_CLK, Y_DO);
  }
  if ((axis.piezoPosition >= axis.oldPiezoPosition - calibrateRange) && (axis.piezoPosition <= axis.oldPiezoPosition + calibrateRange)) {
    if (axis.startTime == 0) {
      axis.startTime = millis();
    } else if (millis() - axis.startTime >= duration) {
      // Serial.println("Positioner stopped moving");
      if (axisIndex == 0) {  // X-Axis
        write_freqs(0, startingFrequencyY);
        axes[0].offsetVal = axis.piezoPosition;
      } else if (axisIndex == 1) {  // Y-Axis
        write_freqs(0, 0);
        axes[1].offsetVal = axis.piezoPosition;
      }
      axis.calibrationDone = true;
      write_freqs(0, 0);  // Temporarily stops movements - calibration is done
      // Serial.print("Finished calibrating axis ");
      // Serial.println(axisIndex);
    }
  } else {
    axis.startTime = 0;
  }

  axis.oldPiezoPosition = axis.piezoPosition;
  delay(100);
}

bool receivingCoords = false;
int coordCount = 0;

void readSerialInput() {
  if (Serial.available() > 0) {
    String line = Serial.readStringUntil('\n');
    line.trim();

    if (line == "START_COORDS") {
      // Serial.println("Ready to receive coordinates");
      receivingCoords = true;
      coordCount = 0;
      return;
    }

    if (line == "END_COORDS") {
      // Serial.print("Received ");
      // Serial.print(coordCount);
      // Serial.println(" coordinates total.");
      receivingCoords = false;
      readComplete = true;  // Coordinate reading done 
      return;
    }
    if (receivingCoords) {
      int commaIndex = line.indexOf(',');
      if (commaIndex > 0) {
        String xStr = line.substring(0, commaIndex);
        String yStr = line.substring(commaIndex + 1);
        float xVal = xStr.toFloat();
        float yVal = yStr.toFloat();

        // Store or process coordinate
        coordinates[coordCount].xMicrons = xVal;
        coordinates[coordCount].yMicrons = yVal;
        coordinates[coordCount].xCounts = xVal / countsToMicrons;
        coordinates[coordCount].yCounts = yVal / countsToMicrons;

        coordCount++;
        // Serial.println("ACK");
      }
    }
    
  }
}

void display_position(){
  // TRACKING X POSITION
  axes[0].newPiezoPosition = position_read(X_CS, X_CLK, X_DO);
  axes[0].piezoPosition = track_position(axes[0].piezoPosition, axes[0].newPiezoPosition, axes[0].oldPiezoPosition, 0, true, axes[0].offsetVal);
  axes[0].oldPiezoPosition = axes[0].newPiezoPosition;

  // TRACKING Y POSITION
  axes[1].newPiezoPosition = position_read(Y_CS, Y_CLK, Y_DO);
  axes[1].piezoPosition = track_position(axes[1].piezoPosition, axes[1].newPiezoPosition, axes[1].oldPiezoPosition, 1, true, axes[1].offsetVal);
  axes[1].oldPiezoPosition = axes[1].newPiezoPosition;
  Serial.print("X");
  Serial.print(axes[0].piezoPosition * countsToMicrons);
  Serial.print(";");
  Serial.print("Y");
  Serial.println(axes[1].piezoPosition * countsToMicrons);  
}

bool closed_loop_positioning(int targetX, int targetY){
  int limit = 500;
  executionDuration = micros() - lastExecutionTime;
  lastExecutionTime = micros();

  // --------- X Axis ---------
  if ((abs(axes[0].piezoPosition - previousPiezoPositionX) > MIN_VEL_COMP_COUNT) || (micros() - previousVelCompTimeX) > MIN_VEL_COMP_TIME) {
    piezoVelocityX = (double)(axes[0].piezoPosition - previousPiezoPositionX) * 1000000 / (micros() - previousVelCompTimeX);
    previousPiezoPositionX = axes[0].piezoPosition;
    previousVelCompTimeX = micros();
  }
  positionErrorX = targetX - axes[0].piezoPosition;
  integralErrorX += positionErrorX * (float)(executionDuration) / 1000000;
  velocityErrorX = 0 - piezoVelocityX;
  desiredFrequencyX = KP * positionErrorX + KI * integralErrorX + KD * velocityErrorX;

  if (desiredFrequencyX >= limit) desiredFrequencyX = limit;
  else if (desiredFrequencyX <= -limit) desiredFrequencyX = -limit;
  else if ((desiredFrequencyX >= 0) && (desiredFrequencyX <= 10)) desiredFrequencyX = 3;
  else if ((desiredFrequencyX <= 0) && (desiredFrequencyX >= -10)) desiredFrequencyX = -3;

  // --------- Y Axis ---------
  if ((abs(axes[1].piezoPosition - previousPiezoPositionY) > MIN_VEL_COMP_COUNT) || (micros() - previousVelCompTimeY) > MIN_VEL_COMP_TIME) {
    piezoVelocityY = (double)(axes[1].piezoPosition - previousPiezoPositionY) * 1000000 / (micros() - previousVelCompTimeY);
    previousPiezoPositionY = axes[1].piezoPosition;
    previousVelCompTimeY = micros();
  }
  positionErrorY = targetY - axes[1].piezoPosition;
  integralErrorY += positionErrorY * (float)(executionDuration) / 1000000;
  velocityErrorY = 0 - piezoVelocityY;
  desiredFrequencyY = KP * positionErrorY + KI * integralErrorY + KD * velocityErrorY;

  if (desiredFrequencyY >= limit) desiredFrequencyY = limit;
  else if (desiredFrequencyY <= -limit) desiredFrequencyY = -limit;
  else if ((desiredFrequencyY >= 0) && (desiredFrequencyY <= 10)) desiredFrequencyY = 10;
  else if ((desiredFrequencyY <= 0) && (desiredFrequencyY >= -10)) desiredFrequencyY = -10;

  write_freqs(-desiredFrequencyX, desiredFrequencyY);

  // Target position check (both axes within TARGET_BAND)
  bool xReached = abs(axes[0].piezoPosition - targetX) <= TARGET_BAND;
  bool yReached = abs(axes[1].piezoPosition - targetY) <= TARGET_BAND;

  return xReached & yReached;
}
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

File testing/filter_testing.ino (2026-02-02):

#include <Arduino.h>
#include <timers.h>
#define DEADBAND 1.0F

template <int order> // order is 1 or 2
class LowPass
{
  private:
    float a[order];
    float b[order+1];
    float omega0;
    float dt;
    bool adapt;
    float tn1 = 0;
    float x[order+1]; // Raw values
    float y[order+1]; // Filtered values

  public:  
    LowPass(float f0, float fs, bool adaptive){
      // f0: cutoff frequency (Hz)
      // fs: sample frequency (Hz)
      // adaptive: boolean flag, if set to 1, the code will automatically set
      // the sample frequency based on the time history.
      
      omega0 = 6.28318530718*f0;
      dt = 1.0/fs;
      adapt = adaptive;
      tn1 = -dt;
      for(int k = 0; k < order+1; k++){
        x[k] = 0;
        y[k] = 0;        
      }
      setCoef();
    }

    void setCoef(){
      if(adapt){
        float t = micros()/1.0e6;
        dt = t - tn1;
        tn1 = t;
      }
      
      float alpha = omega0*dt;
      if(order==1){
        a[0] = -(alpha - 2.0)/(alpha+2.0);
        b[0] = alpha/(alpha+2.0);
        b[1] = alpha/(alpha+2.0);        
      }
      if(order==2){
        float alphaSq = alpha*alpha;
        float beta[] = {1, sqrt(2), 1};
        float D = alphaSq*beta[0] + 2*alpha*beta[1] + 4*beta[2];
        b[0] = alphaSq/D;
        b[1] = 2*b[0];
        b[2] = b[0];
        a[0] = -(2*alphaSq*beta[0] - 8*beta[2])/D;
        a[1] = -(beta[0]*alphaSq - 2*beta[1]*alpha + 4*beta[2])/D;      
      }
    }

    float filt(float xn){
      // Provide me with the current raw value: x
      // I will give you the current filtered value: y
      if(adapt){
        setCoef(); // Update coefficients if necessary      
      }
      y[0] = 0;
      x[0] = xn;
      // Compute the filtered values
      for(int k = 0; k < order; k++){
        y[0] += a[k]*y[k+1] + b[k]*x[k];
      }
      y[0] += b[order]*x[order];

      // Save the historical values
      for(int k = order; k > 0; k--){
        y[k] = y[k-1];
        x[k] = x[k-1];
      }
  
      // Return the filtered value    
      return y[0];
    }
};


// MAGNETIC SENSOR INITIALIZATION
const int X_CS = A2;
const int X_CLK = A3;
const int X_DO = A4;
const int Y_CS = A5;
const int Y_CLK = 25;
const int Y_DO = 24;

// STATE MACHINE
const int CALIBRATE = 1;
const int READ = 2;
const int MOVE = 3;
const int OPEN = 4;
const int WAIT = 5;
// int state = CALIBRATE;
int old_state = CALIBRATE;
bool axis_state = 0;       // 0 is X axis, 1 is Y axis
bool unusedXFlag = true;   // For tracking if offset is used
bool unusedYFlag = true;   // For tracking if offset is used
bool readComplete = false; // Checks if reading is complete before moving stages

// CALIBRATION
struct AxisStatus {
  volatile int piezoPosition;
  volatile int oldPiezoPosition;
  volatile int newPiezoPosition;
  volatile int offsetVal;
  bool calibrationDone;
  unsigned long startTime;
};

// INITIALIZING POSITION TRACKING
#define NUM_AXES 2  // X, Y
AxisStatus axes[NUM_AXES] = {
  { -15000, 0, 0, 0, false, 0 },  // X
  { -15000, 0, 0, 0, false, 0 },  // Y
};
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

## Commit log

2025-11-03 Add files for jlc_pcb order
    [Nanopositioner_V10-B_Cu.gbr, Nanopositioner_V10-B_Fab.gbr, Nanopositioner_V10-B_Mask.gbr, Nanopositioner_V10-B_Paste.gbr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]
2025-11-03 Add KICAD files
    [nanopositioner_pcb.kicad_pcb, nanopositioner_pcb.kicad_sch]
2025-11-03 Electronic components (ie driver, power supply, microcontroller)
    [PJ-002B.step, PiezoDrive.PcbLib, PiezoDrive.SchLib]
2025-11-03 Create cad and assembly file
2025-11-03 Added stl files of full CAD
    [piezo_actuator_mount.stl, sample_stage.stl, x_stage.stl, y_stage.stl]
2025-11-03 Add Fusion360 files of full CAD
    [nanopositioner_assembly.f3z, piezo_actuator_mount.f3d, sample_stage.f3d, x_stage.f3d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]
2025-11-03 Add bill of materials
2026-01-10 controller v2 pcb design in kicad
    [nano_core_v2.kicad_pcb, nano_core_v2.kicad_sch]
2026-01-10 sensor head v1 in kicad
    [sensor_head_v2.kicad_pcb, sensor_head_v2.kicad_sch]
2026-01-10 sensor_head v2 order for jlcpcb
    [sensor_head_v2-B_Cu.gbr, sensor_head_v2-B_Mask.gbr, sensor_head_v2-B_Paste.gbr, sensor_head_v2-B_Silkscreen.gbr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]
2026-01-10 nano_core v2 order for jlcpcb
    [nano_core_v2-B_Cu.gbr, nano_core_v2-B_Mask.gbr, nano_core_v2-B_Paste.gbr, nano_core_v2-B_Silkscreen.gbr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]
2026-02-02 Add sensor data processing and visualization script
    This script processes sensor data from Keyence and Arduino, identifies global extremes, selects turning points, and exports the processed data along with visualizations.
2026-02-02 Add sensor error processing and analysis script
    This script processes sensor data from Keyence and Arduino, calculates errors, and generates time domain and FFT analysis plots.
2026-02-02 Examples of collected data
    [keyence_output10.csv]
2026-02-02 Add LowPass filter and sensor handling in Arduino sketch
    This commit introduces a LowPass filter class for signal processing in an Arduino sketch. It includes initialization of magnetic sensors, state machine logic, and methods for handling position tracki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
2026-02-27 Add resolution_test.ino for low pass filter implementation
2026-02-27 Add resolution_plot.py for sensor data visualization (paired with resolution_test.ino)
    This script imports sensor data, processes it, and generates plots for raw sensor data and mirror error analysis.
2026-02-28 Updated position tracking for robustness and update calibration range
    Added position tracking functionality and adjusted calibration parameters.
2026-03-04 Update positioning logic (combining magnetic and posic encoder)
    Added a MovingAverage class for filtering and updated coordinate structure to include new fields for magnetic and positional counts. Adjusted the closed loop positioning function to accommodate the n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
2026-03-28 Improved repeatability and accuracy performance
    Refactor state machine and coordinate handling in resolution_test.ino. Update encoder tracking and calibration parameters.
